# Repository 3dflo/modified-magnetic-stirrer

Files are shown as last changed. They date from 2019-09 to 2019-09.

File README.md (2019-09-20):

<p align="center">
<h1 align="center">Creating a great bioreactor for everyone!</h1>
</p>

## Hello!
Welcome to the Magnetic Stirrer project repository! It started in the year 2019 as an universtity project. We work on a low cost, open source bioreactor with a volume up to 4 l. As one sub-project, a low friction stirrer with multiple replaceable stirrer geometries is developed by modifying a simple commercial magnetic stirrer. It is supposed to work as a stand-alone stirrer as well as to be controlable via web interface.

Software and hardware will be described later. If you are interested, you can read a bit more about the idea behind the project in this README.

You can directly jump to the sections:

- [How everything started](#how-everything-started)
- [A bit of background](#why-should-you-care-about-this-bioreactor)
- [What's to solve?](#let-me-present-to-you-the-problem)
- [How to build the modified magnetic stirrer](#how-to-build-the-modified-magnetic-stirrer)
- [Who is behind all this?](#who-is-behind-all-this)

## How everything started
We are a group of Master students in the field of life sciences. With the opening of the new student's Makerspace at our campus, a Makerspace-related class should be launched at the same time. A lot of steps took place in a short time and soon, a team was found to participate in the first class taking place as a pilot project. 

## Why should you care about this bioreactor?
Laboratory scaled bioreactors are part of several lab courses at university. But as most courses are only meant to be half-day events, it was not possible to observe and compare the growing of microorganisms in live until now. For that purpose, we want to develop a system, which may be controled and observed via an web interface. For providing this sytem with only low costs, the bioreactor is constructed by material available in almost every lab as well as by self-created tools, perfectly adapted for the named application. Additionally, the communication will be realized by a bus-system.

## Let me present to you: The Problem
The main reason to develop this bioreactor system is to provide to the students a possibility to observe the microorganisms' activity in real time while only beeing present at course half of the day, as described before. But why should you care about the stirrer? The stirrer is not only responsible for creating a homogenous environment concerning nutrients, waste materials, gas, fermentation products but also microorganisms. It is furthermore necessary to guarantee the delivery of oxygen out of air for aerob processes. Nevertheless, some products and cells are very sensitive to friction. As commercial magnets for magnetic stirrers are used to lay on the ground while stirring, a high friction results and might lead to significant losses in product or cell number. Additionally, adapting the stirrer geometry to the explicit system can improve the fermentation's results. Therefore, a flexible stirrer is developped, which may be driven by a commercial magnetic stirrer, but which provides a low friction stirring solution with several replaceable stirrer geometries such as disks or propellers.

## How to build the modified magnetic stirrer

Let's start to build it.

Have a look at the [Step-by-step Guide](https://github.com/3DFlo/modified-magnetic-stirrer/blob/master/Step-by-step-introduction.md).

Pictures and more informations:

First you need to have a look at the 3D comonents and if they fit your need. You probably have to modify the torque support for the servo motor [Drehmomentstütze.stl](https://github.com/3DFlo/modified-magnetic-stirrer/blob/master/Hardware/Drehmomentst%C3%BCtze.stl). 
The rest of the parts can be found under [Hardware](https://github.com/3DFlo/modified-magnetic-stirrer/tree/master/Hardware). These have to be 3D printed. The Hybrid_Stevenrohr.stl together with Scheibe.stl should be combined with a so called Stevenrohr (sterntube in english). This is the main part of the stirrer:

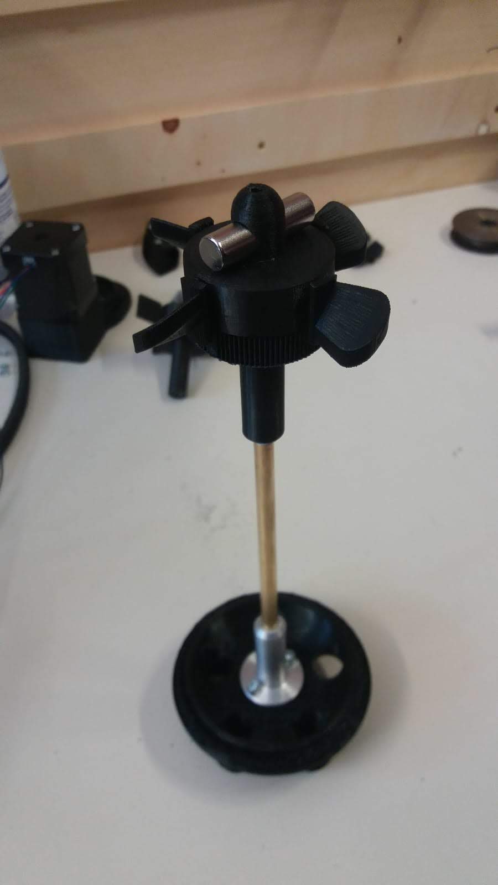
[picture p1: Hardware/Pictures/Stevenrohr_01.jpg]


Now the servo motor can be combined with the torque support:

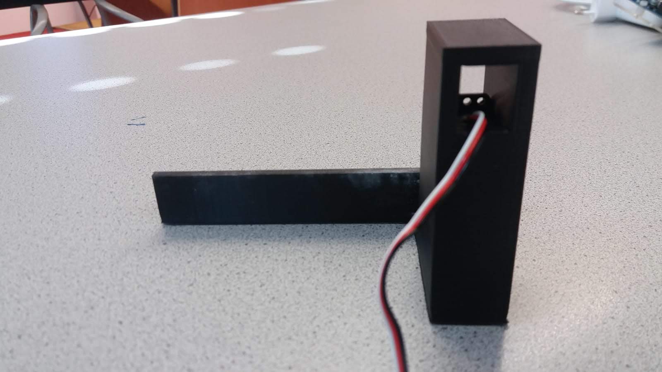
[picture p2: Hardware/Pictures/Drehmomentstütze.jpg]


At last the hall sensor has to be added to the lower side of the magnetic stirrer. The sensor has to be very close to the magnets in the stirrer. Otherwise it wont work!

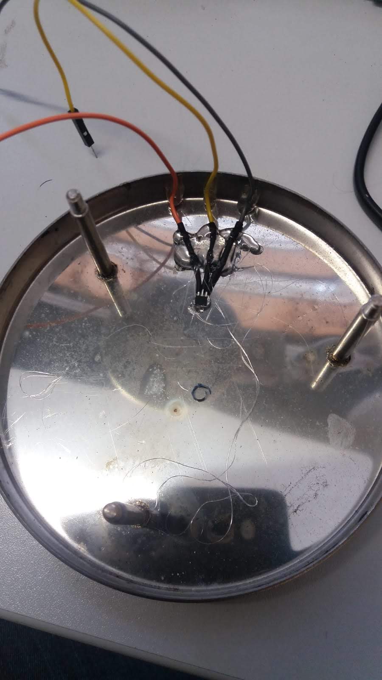
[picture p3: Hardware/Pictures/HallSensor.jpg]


All parts have to be combined with the arduino uno like this:

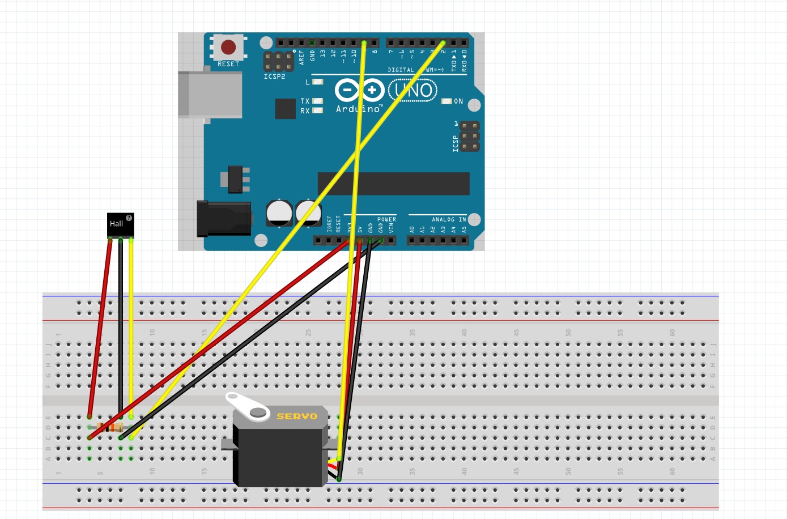
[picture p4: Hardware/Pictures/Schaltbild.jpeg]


The final version should look something like this:

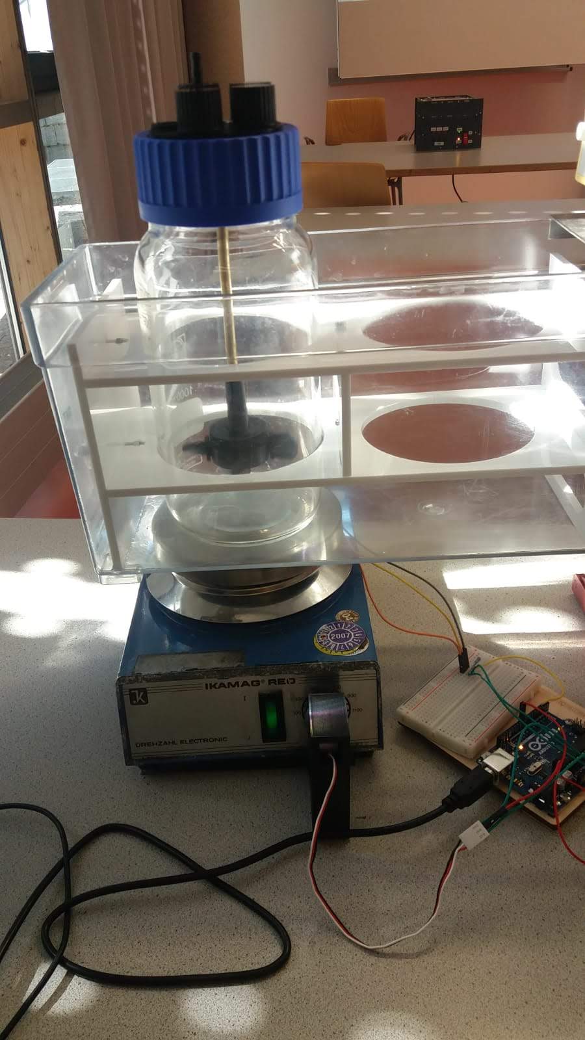
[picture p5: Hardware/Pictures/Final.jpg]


At last, load the software on the ardunio and test it.
Have fun!

## Who is behind all this?
We are students at the Technical University of Munich [university website](https://www.tum.de/nc/en/).

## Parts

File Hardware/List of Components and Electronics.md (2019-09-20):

This is the list of the used components:

<!-- tocstop -->

## Components

### What you need for your own stirrer
- Filament for 3D printer (we used PLA for the objects and PVA as support)
- Commercial magnetic stirrer
- Shaft system for model construction, so called sterntube (Graupner Wellenanlage (Ø x L) 3 mm x 130 mm M4)
- Neodym bar magnet 8 x 30 mm, Grade N42
- 2x screw (M3 x 8), nut and washer M3
- Washer M4

### For controlling the stirrer via web interface:
- Arduino Uno
- MX485
- Hall sensor
- plug circuit board
- servo motor
- electrical resistance 10 kOhm
- 9 wires
- tin solder

### Tools and devices
- 3D printer
- drilling machine
- soldering iron
- hot glue gun
- thread cutter (M4)
- files
- allen key 2.5

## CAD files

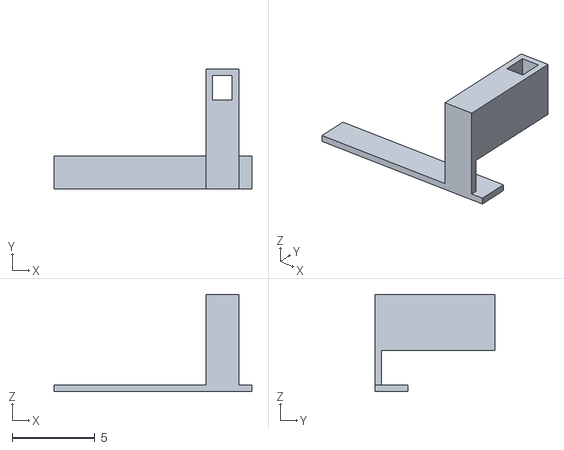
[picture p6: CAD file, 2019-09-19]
Hardware/Drehmomentstütze.stl
12.0 x 7.30 x 5.90

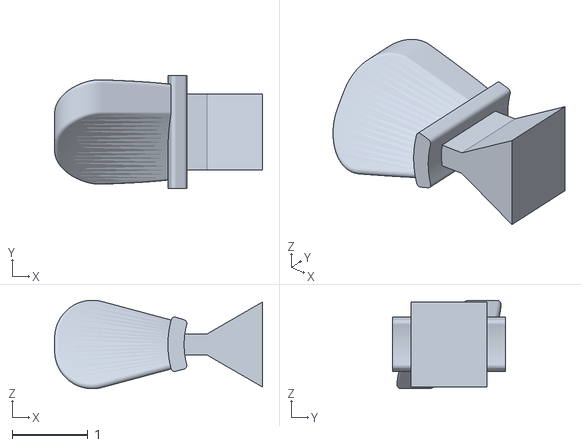
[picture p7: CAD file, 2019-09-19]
Hardware/Rührergeometrie_Propeller_abwärts_Spiel.stl
2.75 x 1.50 x 1.17

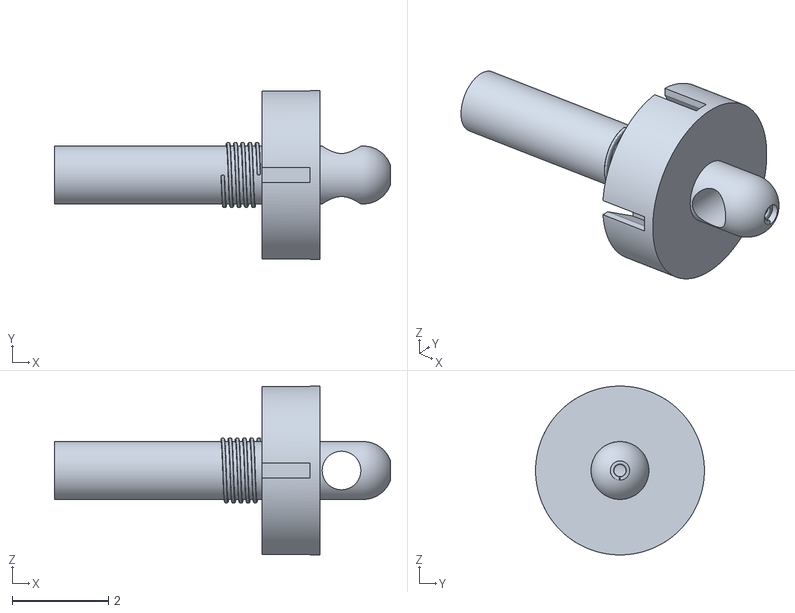
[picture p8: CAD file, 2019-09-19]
Hardware/Hybrid_Stevenrohr.stl
6.97 x 3.50 x 3.50

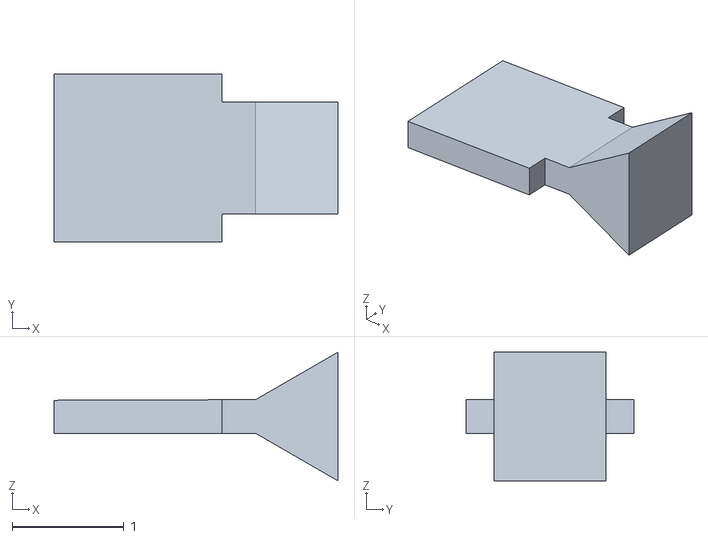
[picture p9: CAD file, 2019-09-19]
Hardware/Scheibengeometrie_einfach.stl
2.54 x 1.50 x 1.15

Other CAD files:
Hardware/Rührergeometrie_Propeller_aufwärts_Spiel.stl
Hardware/Drehmomentstütze.ipt
Hardware/Hybrid_Stevenrohr.ipt
Hardware/Rührergeometrie_Propeller_abwärts_Spiel.ipt
Hardware/Rührergeometrie_Propeller_aufwärts_Spiel.ipt
Hardware/Scheibe.ipt
Hardware/Scheibengeometrie_einfach.ipt

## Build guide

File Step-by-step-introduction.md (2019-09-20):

## Step-by-step-introduction

How to create YOUR OWN modified magnetic stirrer

### 1. 3D-models and hardware

- Choose your magnetic stirrer and the bottle you want to use as a fermenter

- Choose your stirrer geometries

- Buy a shaft system and a bar magnet

- Choose and buy the filament for your 3D-printer

- Measure and determine your geometric dimensions

- Create your 3D models with any software (we used AutoDesk Inventor Professional)

You need to create the agitator shaft, the stirrer geometries, the shaft nut and your torque support

- Test the ideal settings for your 3D-printer

- Start the first test prints

- Improve your models and print at least your final version

- Assembly together the single stirrer parts

- Drill and tap an M4 threaded hole into your shaft to connect the shaft system with the printed agitator shaft

- Drill two holes into the cap to fix the shaft system and fix it with two screws and nuts

- Screw the cap on the bottle and put it onto your magnetic stirrer and test the function

- Your mechanical work is done 😊

### 2. Electronics and software

- Buy your electronic components and make sure you have all your tools

- Connect your electronics (see our electrical layout)

- Write your code (you can use ours as orientation, but there is of course still potential for improvements)

- Test your system and program (you need to hold the hall sensor close to the magnet)

- If Everything works, put the motor into the torque support and fix the torque support at the magnetic stirrer

- Stick the hall sensor onto the magnetic stirrer close to the magnet but not in the center

- Connect everything again and see your stirrer working 😊

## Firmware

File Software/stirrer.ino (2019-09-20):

/*
   RPM Informations: http://www.arduinotutorialonline.com/2017/12/a-simple-guide-to-using-hall-sensor.html
   Modbus https://github.com/Mrdayday/Online-submerged-photometer/blob/master/Software/Photometer.ino
   BlinkWithoutDelay from Arduino IDE
*/

#include <ModbusRtu.h>   // Modbus Package by smarmengol(Github)
#include <Servo.h> //Servo Package
Servo myServo;
// assign the Arduino pin that must be connected to RE-DE RS485 transceiver
#define TXEN  4  // Pinnumber for Modbus


Modbus slave(2, 0, TXEN); //Modbus object, Information about: Slave adress, Bus System (1=RS485), Connected PIN
uint16_t rotordata[3] = {0, 0, 0}; //Array for Modbus
/* Two currently used values and one free/blank
   rotordata[0]= Given speed by Master
   rotordata[1]= Current speed
   rotordata[2]= Availability Check; 0 -> standalone version
*/

// Fixed Falues
const unsigned long calculationTime = 6000; //Time between two RPM calculations

int potVal = 0;
int newpotVal = 0;
int angle;
long previousMillis = 0;        // will store last time LED was updated
//long calculationTime = 6000;           // calculationTime at which to blink (milliseconds)

//RPM Detection
const int hallSensorPin = 2;                      // connect the hall effect sensor on pin 2
int rpmDetected = 0;
int count = 0;
boolean countFlag = LOW;

void setup() {
  // put your setup code here, to run once:
  myServo.attach(9); //defines output for Servo (9 and 10 available at Arduino)
  slave.begin(19200);
  Serial.begin(9600); //connection to console with Baud-number of 9600
  Serial.print("Please type in a number between 0 to 7! \"Kein Zeilenende\" has to be activated\n");
}

void loop() { //Main code
  unsigned long currentMillis = millis(); //Milliseconds for timer for specific actions
  slave.poll(rotordata, 3); //write and recive data
  if (digitalRead(hallSensorPin) == HIGH) //Hall Sensor is not near a magnet
  {
    countFlag = HIGH;
  }
  if (digitalRead(hallSensorPin) == LOW && countFlag == HIGH) // Hall Sensor is near a magnet after no magnet
  {
    count++;
    countFlag = LOW;
  }

  potVal = setRPM(&newpotVal); //New rpm setting

  //RPM calculation and sending to servo://
  if (currentMillis - previousMillis >= calculationTime) {
    // save the last time
    previousMillis = currentMillis;
    rpmDetected = int(60000 / float(calculationTime)) * count; //Calculation of RPM
    showRPM(rpmDetected);
    count = 0;
    if ((rpmDetected > potVal + 20 ) || (rpmDetected < potVal - 20)) {
      newpotVal = changeSpeed(rpmDetected, potVal, newpotVal);
    }
    potVal = newpotVal;
    angle = map(potVal, 700, 0, 0, 179); // Speed to Angle in the servo controller
    myServo.write(angle);
  }
}

int setRPM(int* newpotVal) {
  if (rotordata[2] != 0) //Availability Check
  {
    potVal = rotordata[1]; //Angle of the array rotordata[1]
    if (potVal == 0) { //If rpm set to 0 go to 0 direclty
      *newpotVal = 0;
      //Serial.print("new set RPM to 0= ");//for testing
      //Serial.print(*newpotVal);//for testing
    }
    return potVal;
  }
  else if (Serial.available() > 0) {
    potVal = Serial.read() - 48;
    if (potVal > 7 || potVal < 0) {
      Serial.print("Please type in a number between 0 to 7! \"Kein Zeilenende\" has to be activated\n");
    } else
    {
      if (potVal == 0) { //If rpm set to 0 go to 0 direclty
        *newpotVal = 0;
        //Serial.print("new set RPM to 0= ");//for testing
        //Serial.print(*newpotVal);//for testing
      }
      Serial.println((String)"RPM set to: " + potVal + "00");
      return potVal * 100;
    }
  }

  //Possible alternatives for different standalone version could be a potentiometer or a small keypad directly attached to the arduino
}

void showRPM(int rpm) // For debugging and checking the speed
{
  Serial.print("RPM = ");
  Serial.print(rpm);
  Serial.print("\n ");
}

//RPM change depending on real RPM//
int changeSpeed(int rpmDetected, int potVal, int newpotVal) {
  if (newpotVal < 700) {
    if (rpmDetected  < potVal) { //RPM is to low and needs to be higher
      potVal = newpotVal + 20;
      //Serial.print("new set RPM in backgroud= "); // For debugging and checking the speed
      //Serial.print(potVal);// For debugging and checking the speed
      //Serial.print("\n ");// For debugging and checking the speed
      return potVal;
    }
  }
  if (newpotVal > 0) {
    if (rpmDetected  > potVal) {
      potVal = newpotVal - 10; //RPM is to high and needs to be lower
      //Serial.print("new set RPM in backgroud= ");// For debugging and checking the speed
      //Serial.print(potVal);// For debugging and checking the speed
      //Serial.print("\n ");// For debugging and checking the speed
      return potVal;
    }
  }
}

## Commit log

2019-08-23 Create Bill of Material
2019-08-23 Update Bill of Material
